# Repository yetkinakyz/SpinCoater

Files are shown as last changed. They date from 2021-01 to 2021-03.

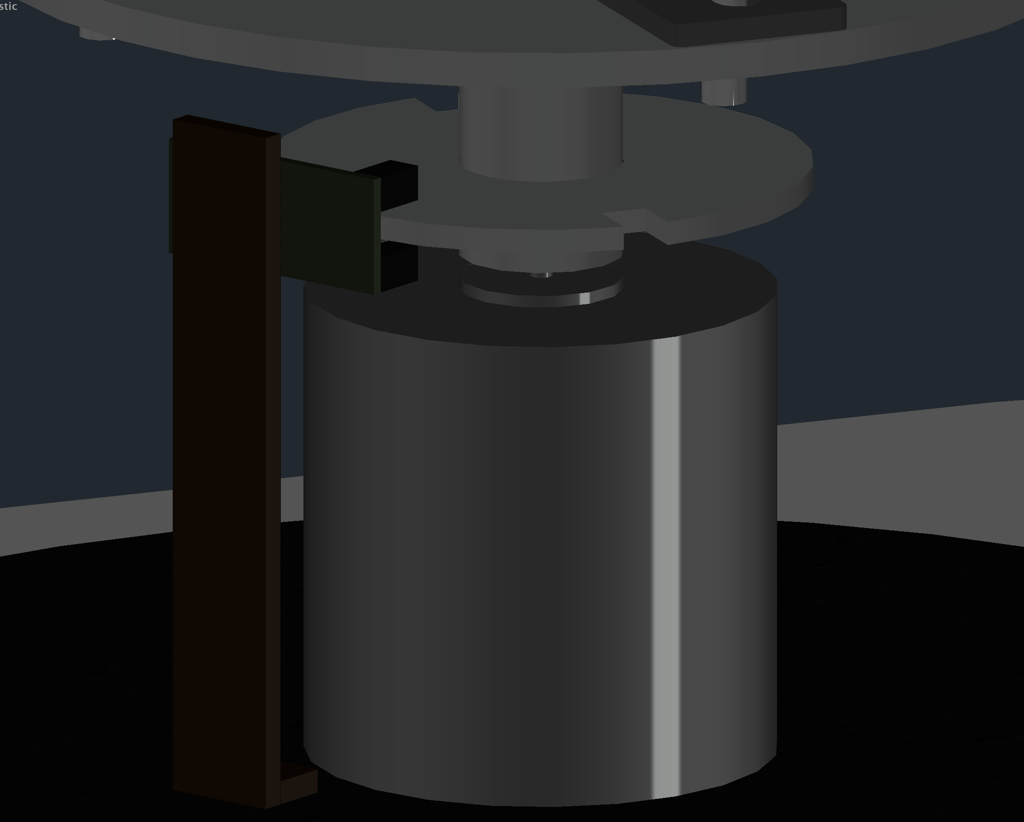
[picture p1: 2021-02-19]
Design/Images/7.png

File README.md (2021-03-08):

# Design and Fabrication of a Cost-Effective Spin Coater

## Project Video

Cost-Effective Spin Coater Project (http://www.youtube.com/watch?v=7xUjQFKw6QM "Project Video")

## About The Project

### Summary

The main objective of this project is design and fabrication of a cost-effective spin coater for depositing thin films.

The originality of this project is that its design and source code are completely free, usable and modifiable, and the production of a spin coater device is substantially inferior to those available in the market.

This project aims that supporting the free software philosophy through the completely free and open- source design having MIT License, making the product accessible to a wider audience than those sold in the market thanks to low cost, and reinforcing the knowledge gained through engineering education with an engineering design project and completing the deficiencies.

### Literature

The spin coating method is a commonly used coating method to obtain uniform thin material films, usually polymers, on the surface of a substrate using the concept of centrifugal force. This method, which is easy to use, safe and inexpensive, is highly preferred for many applications where high quality layers are required such as microcircuit manufacturing, compact discs, magnetic disk coatings, polymer electronic devices [1].

The cost of commercial rotary coating devices can range from about 600 to 4000 $ In addition to having a high price, commercial rotary coating devices need a specialist for maintenance and repair. Therefore, a low cost and open source rotary coating device is in demand for academic work and student education, with performance similar to a commercial model in the laboratory [2].

The aim of this study is to design an easily repairable, open source spin coater device with functions similar to commercial devices, such as being able to rotate up to 7200 RPM for 3600 seconds and be programmable at a cost of less than 65 $, as well as commercial devices. At the same time, it is aimed to support the free software philosophy by sharing the entire project design free of charge under the MIT license.

### Method

The device control is provided by the 2x16 LCD screen and 6 buttons on the device. Raspberry Pi Zero Wireless is used as a development board in order to enable the device to perform all desired functions. As the operating system, Raspberry Pi OS, a Linux-based operating system, is used and the control software is written in Python. Some scripts used is written with Bash.

The card is powered by a 5V 3A adapter. The STD MTR QK1-4640 24V 9000 RPM DC motor, which enables the surface to be coated to rotate, is chosen arbitrarily in line with the available facilities and was provided free of charge. L298 motor driver circuit, which drives the motor, can take in enough speed and it is the most affordable driver circuit solding in Turkey. The motor and driver circuit are powered by a 19V 3.42A Adapter and provide the required power for the desired performance. The speed of the engine is measured with the LM393 integrated infrared speed sensor circuit, and a control system is used to keep the engine speed constant at the desired speed by using the signals received from the sensor. Plastic junction box with dimensions of 210mm x 280mm x 138.5mm is preferred for the outer casing of the device in terms of its flexible structure and strength. The disc which the surface to be coated sits, the parts which holds the surface and the disc which is used to count the motor speed are produced by 3D printing. For the transparent inner wall and outer cover for protection purposes, the plastic transparent bowl and plastic pot, which are easily available from the market, were cut and used in appropriate sizes.

The device is ready for use approximately 27 seconds after it is turned on. Up to 10 stages can be defined while programming the device. The device is able to reach the desired speed within an average of 5 seconds and keep it constant with an average of 6% margin of error. It is possible that the error can go down to 2% at high speeds.

The device has been tested with a transparent PVC coating of 2mm thickness and 2x2 cm dimensions. Aceton-diluted nail polish was used as coating material.

### References

[1] Bianchi, R., Pansierra, M., Lima, J., Yagura, L., Andrade, A. Faria, R. 2006. “Spin coater based on brushless dc motor of hard disk drivers”, Progress in Organic Coatings, 57, 33-36.

[2] Sadegh-cheri,M.2016. “Design,Fabrication,andOpticalCharacterizationofaLow-Costand Open-Source Spin Coater”, J. Chem. Educ., 96, 1268-1272.

## Images

### Result



### Appereance

  

### Rotary Part



### Info

  

### Main Menu

  

### Run Program Menu

 

### Quick Programs Menu

  
 

### Set Manual Program Menu

  

### Circuit Diagram



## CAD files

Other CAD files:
Design/DWG/SpinCoater.dwg

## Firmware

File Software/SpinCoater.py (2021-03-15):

'''
    SPIN COATER PROJECT
                    by Yetkin AKYUZ

    Website: https://yetkinakyuz.com
    Email:   contact@yetkinakyuz.com
'''

##### LIBRARIES #####

import RPi.GPIO as GPIO #RASPBERRY PI GPIO LIBRARY WIKI: https://sourceforge.net/p/raspberry-gpio-python/wiki/Home/
import lcddriver #LCD I2C LIBRARY
import RpmControl as Spinner

import os
import time

##### SETUP #####

versionInfo = "1.1.0"
dateInfo = "25.12.2020"

## DISPLAY
display = lcddriver.lcd()

## GPIO
GPIO.setwarnings(False) #DISABLE WARNINGS
GPIO.setmode(GPIO.BCM) #GPIO PIN NUMBERS (GPIO.BOARD for physical pin numbers.)

## BUTTONS
button1 = 0
button2 = 5
button3 = 6
button4 = 13
button5 = 19
button6 = 26

GPIO.setup(button1, GPIO.IN, pull_up_down=GPIO.PUD_DOWN)
GPIO.setup(button2, GPIO.IN, pull_up_down=GPIO.PUD_DOWN)
GPIO.setup(button3, GPIO.IN, pull_up_down=GPIO.PUD_DOWN)
GPIO.setup(button4, GPIO.IN, pull_up_down=GPIO.PUD_DOWN)
GPIO.setup(button5, GPIO.IN, pull_up_down=GPIO.PUD_DOWN)
GPIO.setup(button6, GPIO.IN, pull_up_down=GPIO.PUD_DOWN)

versionText = "Version:   " + versionInfo
dateText = "Date: " + dateInfo

## MAIN MENU
mainMenu = ["RUN PROGRAM       ",
            "INFO            ",
            "REBOOT DEVICE   "]        

mainMenuAscii = ["             " + " " + chr(124) + chr(62),
                "             " + chr(60) + chr(124) + chr(62),
                "             " + chr(60) + chr(124) + " "]

## INFO MENU
infoMenuLine1 = ["RUN OR SET PROG.",
                 "GET INFORMATION ",
                 "REBOOT OPERATING"]

infoMenuLine2 = ["QUICK OR MANUAL ",
                 "ABOUT PROJECT   ",
                 "SYSTEM          "]

## SET MENU
setMenu = ["QUICK PROGRAMS  ",
            "SET MANUAL PROG."]

setMenuAscii = ["             " + " " + chr(124) + chr(62),
                "             " + chr(60) + chr(124) + " "]

## QUICK MENU
program = 1

quickSpeeds1 = ["STAGE 1", 500, 1000, 2000, 3000, 4000]
quickSpeeds2 = ["STAGE 2", 3500, 4500, 5500, 6500, 7200]

quickSeconds1 = ["STAGE 1", 30, 30, 30, 30, 30]
quickSeconds2 = ["STAGE 2", 180, 180, 180, 180, 180]

## MANUAL MENU
manualStages = 1
manualSecond = 5
manualSpeed = 500

manualSeconds = ["-"]
manualSpeeds = ["-"]

## POSITIONS
menuPosition = 0
setPosition = 0
manualPosition = 0

######
display.lcd_clear()
display.lcd_display_string("SPIN COATER     ", 1) #PRINT LINE 1
display.lcd_display_string("        PROJECT ", 2) #PRINT LINE 2

time.sleep(1)

display.lcd_display_string("BY YETKIN AKYUZ ", 1) #PRINT LINE 1
display.lcd_display_string("yetkinakyuz.com ", 2) #PRINT LINE 2

time.sleep(1)

display.lcd_clear()
display.lcd_display_string("    WELCOME!    ", 1) #PRINT LINE 1

time.sleep(1)

display.lcd_clear()

while True:
    display.lcd_display_string(mainMenu[menuPosition], 1) #PRINT LINE 1
    display.lcd_display_string(mainMenuAscii[menuPosition], 2) #PRINT LINE 2

    if not GPIO.input(button1) and menuPosition > 0:
        display.lcd_display_string("                ", 1) #CLEAN LINE 1
        menuPosition = menuPosition - 1

        time.sleep(0.2)

    elif GPIO.input(button2) and menuPosition < len(mainMenu) - 1:
        display.lcd_display_string("                ", 1) #CLEAN LINE 1
        menuPosition = menuPosition + 1

        time.sleep(0.2)

    elif GPIO.input(button4):
        display.lcd_clear()
        display.lcd_display_string(infoMenuLine1[menuPosition], 1) #PRINT LINE 1
        display.lcd_display_string(infoMenuLine2[menuPosition], 2) #PRINT LINE 2
        time.sleep(2)

    elif GPIO.input(button6):
        display.lcd_clear()
        time.sleep(0.2)

        if menuPosition == 0:
            while True:
                 
                display.lcd_display_string(setMenu[setPosition], 1) #PRINT LINE 1
                display.lcd_display_string(setMenuAscii[setPosition], 2) #PRINT LINE 2

                if not GPIO.input(button1) and setPosition > 0:
                    display.lcd_display_string("                ", 1) #CLEAN LINE 1
                    setPosition = setPosition - 1

                    time.sleep(0.2)

                elif GPIO.input(button2) and setPosition < len(setMenu) - 1:
                    display.lcd_display_string("                ", 1) #CLEAN LINE 1
                    setPosition = setPosition + 1

                    time.sleep(0.2)

                elif GPIO.input(button6):
                    time.sleep(0.2)

                    display.lcd_clear()
                    time.sleep(0.2)

                    if setPosition == 0:
                        display.lcd_display_string("P            RPM", 1) #PRINT LINE 1
                        display.lcd_display_string("             SEC", 2) #PRINT LINE 2

                        while True:
                            display.lcd_display_string("P" + str(program) + " " + str(quickSpeeds1[program]) + "-" + str(quickSpeeds2[program]), 1) #PRINT LINE 1
                            display.lcd_display_string("   " + str(quickSeconds1[program]) + "-" + str(quickSeconds2[program]), 2) #PRINT LINE 2

                            if GPIO.input(button2):
                                display.lcd_display_string("P            RPM", 1) #PRINT LINE 1
                                display.lcd_display_string("             SEC", 2) #PRINT LINE 2

                                if program < len(quickSeconds1) - 1:
                                    program += 1
                                    
                                    time.sleep(0.2)
                                
                                elif program == len(quickSeconds1) - 1:
                                    program = 1

                                    time.sleep(0.2)
                                
                                else:
                                    continue

                            elif not GPIO.input(button1):
                                display.lcd_display_string("P            RPM", 1) #PRINT LINE 1
                                display.lcd_display_string("             SEC", 2) #PRINT LINE 2

                                if program > 1:
                                    program -= 1

                                    time.sleep(0.2)

                                elif program == 1:
                                    program = len(quickSeconds1) - 1

                                    time.sleep(0.2)

                                else:
                                    continue

                            elif GPIO.input(button6):
                                display.lcd_clear()
                                display.lcd_display_string("   PROGRAM: " + str(program) + "   ", 1) #PRINT LINE 1
                                display.lcd_display_string("    STARTING    ", 2) #PRINT LINE 2
                                time.sleep(2)

                                Spinner.setExpectedTime(quickSeconds1[program])
                                Spinner.setExpectedRPM(quickSpeeds1[program])
                                Spinner.FirstStage()

                                Spinner.clear()

                                Spinner.setExpectedTime(quickSeconds2[program])
                                Spinner.setExpectedRPM(quickSpeeds2[program])
                                Spinner.NextStage()                                

                                Spinner.clear()

                                display.lcd_clear()
                                display.lcd_display_string("      DONE      ", 1) #PRINT LINE 1

                                time.sleep(3)

                                break

                            elif GPIO.input(button5):
                                program = 1
                                
                                time.sleep(0.2)
                                break

                            else:
                                continue

                    elif setPosition == 1:   
                        manualStop = False        

                        while True:
                            display.lcd_display_string("NUMBER OF STAGES", 1) #PRINT LINE 1
                            display.lcd_display_string("STAGES: " + str(manualStages), 2) #PRINT LINE 2
                            
                            if not GPIO.input(button1):
                                display.lcd_display_string("STAGES:         ", 2) #CLEAR LINE 2
                                
                                if manualStages < 10:
                                    manualStages += 1
                                    time.sleep(0.2)
                                
                                elif manualStages == 10:
                                    manualStages = 1
                                    time.sleep(0.2)
                                
                                else:
                                    continue
                            
                            
                            elif GPIO.input(button2):
                                display.lcd_display_string("STAGES:         ", 2) #CLEAR LINE 2
                                
                                if manualStages > 1:
                                    manualStages -= 1
                                    time.sleep(0.2)
                                
                                elif manualStages == 1:
                                    manualStages = 10
                                    time.sleep(0.2)
                                
                                else:
                                    continue

                            elif GPIO.input(button3):
                                display.lcd_display_string("STAGES:         ", 2) #CLEAR LINE 2

                                manualStages = 1

                            elif GPIO.input(button5):
                                manualStages = 1
                                manualStop = True
                                break

                            elif GPIO.input(button6):
                                manualStages += 1
                                
                                display.lcd_clear()
                                display.lcd_display_string("   STAGES SET   ", 1) #PRINT LINE 1

                                time.sleep(1)
                                break

                            else:
                                continue
                        
                        for stage in range(1, manualStages):
                            manualSeconds.append(manualSecond)
                            manualSpeeds.append(manualSpeed)

                        display.lcd_clear()

                        while True:
                            for stage in range(1,manualStages):
                                if GPIO.input(button5):
                                    manualStages = 1
                                    manualSeconds = [5]
                                    manualSpeeds = [500]

                                    break

                                else:
                                    while True:
                                        display.lcd_display_string("STAGE " + str(stage), 1) #PRINT LINE 1
                                        display.lcd_display_string("TIME: " + str(manualSeconds[stage]) + " SEC", 2) #PRINT LINE 2
                                        
                                        if not GPIO.input(button1):
                                            display.lcd_display_string("TIME:          ", 2) #CLEAR LINE 2

                                            if GPIO.input(button4):

                                                if manualSeconds[stage] > 5 and manualSeconds[stage] < 3540:
                                                    manualSeconds[stage] += 60

                                                    time.sleep(0.2)
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

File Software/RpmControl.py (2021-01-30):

'''
SPIN COATER PROJECT RPM CONTROL SOFTWARE
                        by Yetkin AKYUZ

    Website: https://yetkinakyuz.com
    Email:   contact@yetkinakyuz.com
'''

##### LIBRARIES #####
import RPi.GPIO as GPIO #RASPBERRY PI GPIO LIBRARY WIKI: https://sourceforge.net/p/raspberry-gpio-python/wiki/Home/
import lcddriver #LCD I2C LIBRARY
import time

##### SETUP ##### 

## DISPLAY
display = lcddriver.lcd()

## GPIO
GPIO.setwarnings(False) #DISABLE WARNINGS
GPIO.setmode(GPIO.BCM) #GPIO PIN NUMBERS (GPIO.BOARD for physical pin numbers.)

# MOTOR
motor_in1 = 23 #MOTOR IN 1
motor_in2 = 24 #MOTOR IN 2

motor_en = 25 #MOTOR SPEED CONTROL PIN

# GPIO outputs
GPIO.setup(motor_in1,GPIO.OUT)
GPIO.setup(motor_in2,GPIO.OUT)
GPIO.setup(motor_en,GPIO.OUT)

# Motor turns clockwise
GPIO.output(motor_in1,GPIO.HIGH)
GPIO.output(motor_in2,GPIO.LOW)

motor=GPIO.PWM(motor_en,1000)

motor.start(0) #MOTOR START SPEED
speed = 0

# IR SENSOR 
ir_sensor = 22 #GPIO PIN

GPIO.setmode(GPIO.BCM)
GPIO.setup(ir_sensor,GPIO.IN)

# get_rpm(channel) variables
sample = 6
count = 0
rpm = 0

RpmError = 0

# set_start() and set_end() variables
start = 0
end = 0

sampleRpmList = [ 500, 800,
            1000, 1200, 1500, 1800,
            2000, 2200, 2500, 2800,
            3000, 3200, 3500, 3800,
            4000, 4200, 4500, 4800,
            5000, 5200, 5500, 5800,
            6000, 6200, 6500, 6800,
            7000, 7200]         
sampleSpeedList = [ 4.7, 6,
                    6.7, 7.5, 8.5, 10,
                    10.5, 11.5, 13, 14.5,
                    15.5, 16.8, 18.5, 20,
                    21.5, 23, 25, 27.5,
                    30, 32, 35.5, 38,
                    40.5, 44.0, 48.0, 53.0,
                    55.5, 60.5]
cycleRpmList= []
cycleList = []

firstStage = True
done = False

expectedRPM = 0
expectedTime = 0

# Getters & Setters
def setExpectedRPM(n):
    global expectedRPM
    expectedRPM = n

def getExpectedRPM():
    return expectedRPM

def setExpectedTime(n):
    global expectedTime
    expectedTime = n
    
def getExpectedTime():
    return expectedTime

## Modules

def clear():
    global sample
    global count
    global rpm
    global start
    global end
    global done
    global firstStage
    global speed
    global RpmError
 
    sample = 6
    count = 0
    rpm = 0
    start = 0
    end = 0
    speed = 0
    RpmError = 25

    done = False
    firstStage = True

    setExpectedRPM(0)
    setExpectedTime(0)

    motor.start(0)
    GPIO.output(motor_in1,GPIO.HIGH)

    display.lcd_clear()

def done():
    global done
    done = True
    GPIO.output(motor_in1,GPIO.LOW)

    exit()
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

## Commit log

2020-11-07 sample value changes
2020-11-19 get_rpm will wait for 3 seconds if motor just started to run
2020-11-19 global sample
2020-11-19 tolarence set +/- 50 RPM
2020-11-19 next stage
2020-11-19 motor stop
2020-11-20 change display sample
2020-12-03 damlaya gösteri
    [2018 3.dwg, 2018.dwg]
2020-12-09 new codes test
    [2018 4.dwg, 2018.dwg]
2020-12-09 set stages lcd 2
2020-12-09 minimum stage is 1
2020-12-09 min & max stage count
2020-12-09 set stage message
2020-12-09 reset stages
2020-12-09 stages + 1
2020-12-10 shift between min and max
    [2018 3.dwg, 2018 4.dwg, 2018.dwg]
2020-12-17 new sample values, new speed change value
    [2018 3.dwg, 2018 4.dwg, 2018.dwg]
2020-12-17 new sample values & speed control changes
2020-12-17 new sample values
2020-12-17 add "Restart Device" selection
2020-12-17 sample values
2020-12-18 Design Update
    [2000.dwg, 2004.dwg, 2007.dwg, 2010.dwg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]
2020-12-18 manualSpeed[stage] reset fix
2020-12-23 set sample & set error functions <=2000 RPM
2021-03-15 print comments fix
